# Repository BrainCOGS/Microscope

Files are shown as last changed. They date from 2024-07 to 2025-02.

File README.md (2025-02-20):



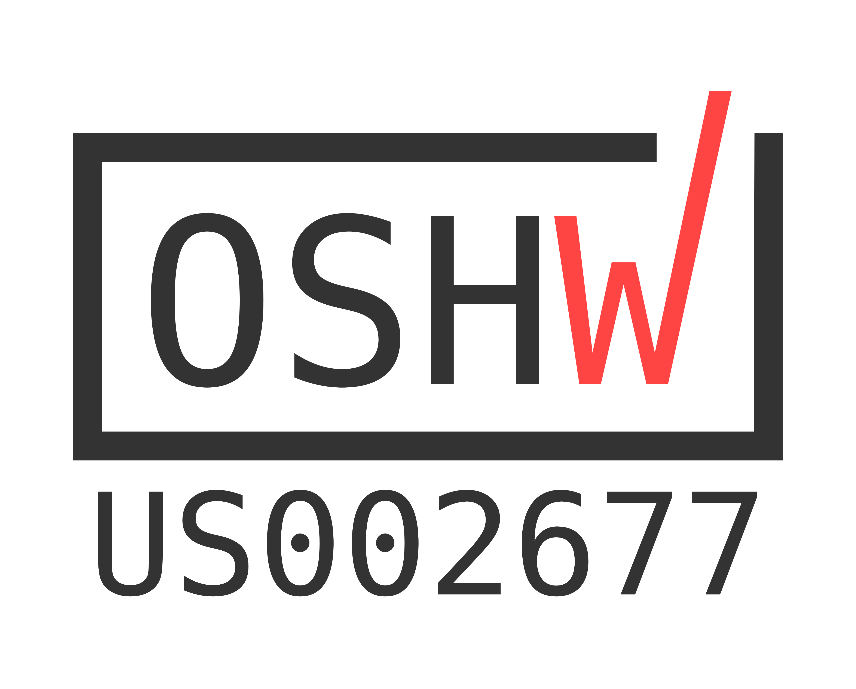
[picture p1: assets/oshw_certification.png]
# Twinkle 

This repository documents a microscope for Two-photon Imaging in Neuroscience, and Kit for Learning and Education — "Twinkle". <br/> It offers an affordable solution for a fully open, high-performance and cost-effective research and teaching microscope. Here, you can find the complete design and documentation. 

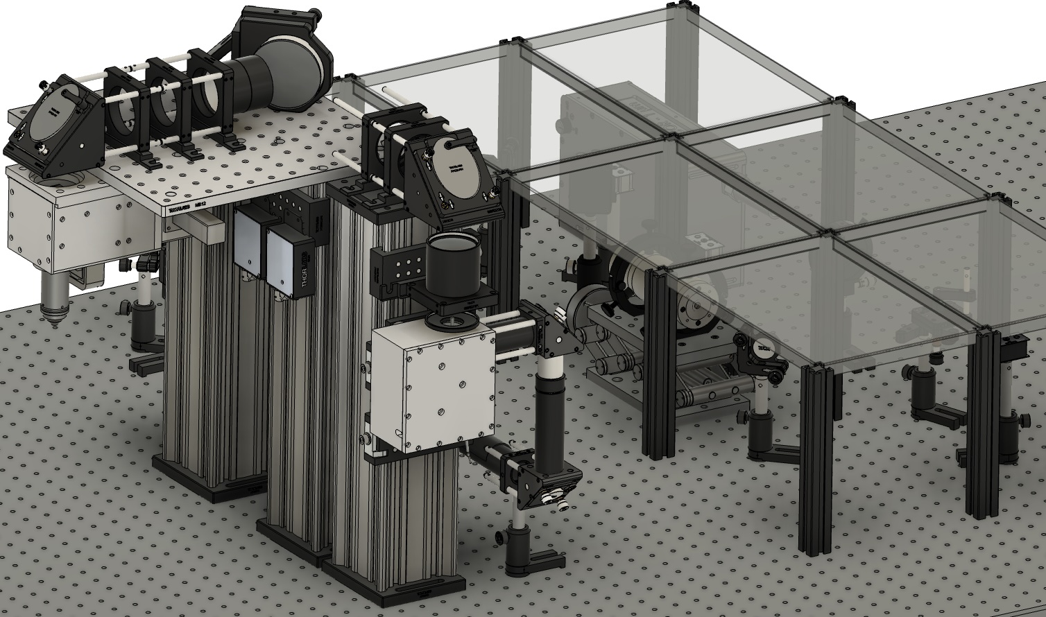
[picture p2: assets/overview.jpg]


### Repository Content
    .
    ├── article                 # Latex code and figures for the main manuscript.
    ├── assets                  # Supporting files, OSHW certification.
    ├── cad                     # Computer-aided design (CAD) files of the entire instrument in various file formats.
    ├── documentation           # Build instructions and supplemental material.
    ├── parts                   # Detailed bill of materials (BoM), important quotes, and drawings for machining.
        ├── Drawings            # Drawings for machining.
        ├── various files       # BoM and important quotes.
    ├── zemax                   # Optics simulations.
        ├── Collection          # Zemax files, drawings, and simulated performance of the collection optics.
        ├── Excitation          # Zemax files, drawings, and simulated performance of the excitation optics.
        ├── matlab              # Matlab scripts, using the Zemax API, measuring the performance of the excitation system.
    ├── LICENSE                 # Text file: This work is licensed under a CC Attribution 4.0 International License.
    ├── README.md               # Text file: This info file.
    └── okh-manifest.yml        # Text file: Open Know-How manifest files.   

### Computer assisted design (CAD) files
The CAD files are provided in two formats:
- In the Fusion 360 native format as `FullAssembly.f3d`; md5 hash `2b449ca0403f2ce7f2882990966d1d5e`.
- For Autodesk Inventor:
    1. When using the Inventor folder, open the master assembly `FullAssembly.iam`.
    2. A zip file of the same data is split into three files. Assemble the data with `cat x?? > FullAssembly.zip`. The file `FullAssembly.zip` is 165 MB with md5 hash `33ba62a7fb04bc53d11bb660787301d2`.

### Issue
Issues are tracked through this repository. For minor updates, just push. For major ones, use a PR. 

### License
This work is free: you can redistribute it and/or modify it under the terms of the Creative Commons Attribution 4.0 International license, version 4 of the License, or (at your option) any later version (CC-BY-4.0). This program is distributed in the hope that it will be useful, but WITHOUT ANY WARRANTY, to the extent permitted by law; without even the implied warranty of MERCHANTABILITY or FITNESS FOR A PARTICULAR PURPOSE. A copy of the License is provided in this repository.  For more details, see <http://www.gnu.org/licenses/>.

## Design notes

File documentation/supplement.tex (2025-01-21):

% Template for PLoS
% Version 3.5 March 2018

\documentclass[10pt,letterpaper]{article}
\usepackage[top=0.85in,left=2.75in,footskip=0.75in]{geometry}

% amsmath and amssymb packages, useful for mathematical formulas and symbols
\usepackage{amsmath,amssymb}
\usepackage{changepage}
\usepackage[utf8x]{inputenc}
\usepackage{textcomp,marvosym}
\usepackage{cite}
\usepackage[usenames,svgnames,table]{xcolor}
\usepackage[colorlinks = true,
            urlcolor = RoyalBlue,
            citecolor = Crimson,
            backref= page]{hyperref}
\usepackage[right]{lineno}
\usepackage{microtype}
\DisableLigatures[f]{encoding = *, family = * }
\usepackage[table]{xcolor}
\usepackage{array}
\newcolumntype{+}{!{\vrule width 2pt}}

\usepackage{figchild}
\usepackage{enumerate}
\usepackage{sidecap}
\usepackage{wasysym}
\usepackage{mathbbol}

% create \thickcline for thick horizontal lines of variable length
\newlength\savedwidth
\newcommand\thickcline[1]{
  \noalign{\global\savedwidth\arrayrulewidth\global\arrayrulewidth 2pt}%
  \cline{#1}%
  \noalign{\vskip\arrayrulewidth}%
  \noalign{\global\arrayrulewidth\savedwidth}%
}

% \thickhline command for thick horizontal lines that span the table
\newcommand\thickhline{\noalign{\global\savedwidth\arrayrulewidth\global\arrayrulewidth 2pt}%
\hline
\noalign{\global\arrayrulewidth\savedwidth}}

% Text layout
\raggedright
\setlength{\parindent}{0.5cm}
\textwidth 5.25in 
\textheight 8.75in

\usepackage[aboveskip=1pt,labelfont=bf,labelsep=period,justification=raggedright,singlelinecheck=off]{caption}

\bibliographystyle{plos2015}
\makeatletter
\renewcommand{\@biblabel}[1]{\quad#1.}
\makeatother

\usepackage{lastpage,fancyhdr,graphicx}
\usepackage{epstopdf}
\pagestyle{fancy}

\fancyhf{}
\rfoot{\thepage/\pageref{LastPage}}
\renewcommand{\headrulewidth}{0pt}
\renewcommand{\footrule}{\hrule height 2pt \vspace{2mm}}
\fancyheadoffset[L]{2.25in}
\fancyfootoffset[L]{2.25in}
\lfoot{\today}

%% Include all macros below
\newcommand{\microns}{~\textmu m~} % ALL UNITS UPRIGHT WITH SPACE
\newcommand{\invivo}{\textit{in vivo}~}
\newcommand{\complexi}{i}
%% END MACROS SECTION

\begin{document}
\vspace*{0.2in}

{
\centering\Large\textbf{Supplemental Online Material} 
}
\newline\newline
This supplemental material to the article ``TWINKLE: An open-source two-photon microscope for teaching and research'' describes the assembly, function and alignment of all parts of the microscope. Technical specifications are provided through the CAD files and the Zemax simulations in the online repository at \url{https://github.com/BrainCOGS/Microscope}.

\tableofcontents
\newpage

\linenumbers

\section{Preface}

\subsection{Safety}
Class 4 lasers are extremely dangerous. A reflection on a surface can be enough to inflict permanent eye damage. Safety protocols must be observed. Consult with your institution's environmental health and safety officer and take proper training before performing any work with a laser system. Learn from people experienced with these devices and work carefully.\newline
During alignment, always wear goggles (ours were ML1 by NoIR LaserShields with an optical density $>7$ in the relevant range around $920\text{ nm}$), remove jewelry and watches, only use non-reflective tools, do not store unnecessary items on the optical table, and use the low laser power (“alignment mode”) whenever possible. Once the assembly progresses further, full power mode is necessary. Extra care must be taken then. Always use Laser Viewing Cards to track the laser. We use Thorlabs VRC4. Always be conscious where the beam is, and where the beam goes. The beam must be terminated in beam blockers and should be shielded whenever possible with opaque plastic or anodized aluminium tubes to increase safety.

\subsection{Miscellaneous tools and tips}
The following tools are used throughout the build process:
\begin{itemize}
    \item A high quality duster to remove any residue from optical surfaces. We use a Miller-Stephenson Aero-Duster Ultra MS-222L, in addition to lens tissues (MC-5, Thorlabs) and Methanol (Sigma-Aldrich).
    \item To glue optical filters we used an extra fast setting epoxy (Hardman Double/Bubble Epoxy). To seal small gaps, we use black silicone putty (V-tie self-setting silicone rubber).
    \item We used either McMaster or Thorlabs screwdrivers and hex keys.
    \item For alignment, we used laser viewing cards (VRC4, Thorlabs), cage system alignment plates (VRC4CPT, Thorlabs), and irises (SM1 Graduated Ring-Actuated Iris Diaphragm, SM1D12C, Thorlabs).
\end{itemize}
%
The following general tips might be of help as well:
\begin{itemize}
    \item Shield the beam as soon as alignment of a particular section is done. This increases safety, and avoids accidentally bumping into aligned components.
    \item \textit{Walking the beam}: Any beam can be aligned through two irises using two mirrors. The first mirror the beam meets is sometimes called the ``position'' mirror as it affects primarily the position of the beam. The second ``angle'' mirror instead primarily affects the angle. Assigning each mirror a separate function (position versus angle) and by adjusting them iteratively, is a good rule of thumb for driving the beam through the 2 irises and eventually hitting a specific point at the desired angle \cite{Thorlabs}. 
    \item Be mindful of reflections from all surfaces. Put back-reflecting component at a slight angle to the beam (e.g. the half wave plate) to avoid back-reflections directly into the laser. The back-reflection can then be caught with an iris placed in front of the laser.
    \item Make sure the beam is at the same height across the table. This can be done with an iris and an IR card. 
    \item Take extra care for directing the beam through the center of all lenses and active optical components.
\end{itemize}

\subsection{Parts and bill of materials}
All custom metal pieces are parts of the CAD assembly of the microscope. Ours were manufactured from aluminium stock in the university machine shop. Aluminium has the added benefit of anodization, which can help control scattered light. An overview of the microscope's cost is shown in Tab.~\ref{tab_costs}. Keep in mind that these prices can significantly change over time, while some products can become unobtainable and need to be replaced with a different or newer model.
%
\begin{table}
\begin{center}
  \begin{tabular}{ l c r } \hline
   \textbf{Item} & \textbf{Info} & \textbf{Cost} \\ \hline
\rowcolor{gray!20} 920 nm fs-pulsed Laser  & Spark Alcor 920 + Warranty & 90 k \\
                   ScanImage DAQ-System \& optimized PC & MBF Bioscience& 20 k \\
\rowcolor{gray!20} Piezo collar & Physik Instrumente & 16 k	\\
            $2\times$ PMTs + preamplifiers  & Hamamatsu \& Thorlabs & 12 k \\
\rowcolor{gray!20} Pockels cell             & Conoptics &	11 k \\
                   Objective                & Nikon &  8 k \\
\rowcolor{gray!20} Machining custom parts   & Machine Shop; as per CAD files &  7 k \\
                   Optical filters          & AVR optics \& Semrock &  7 k \\
\rowcolor{gray!20} Lenses + optomechanics   & Thorlabs \& Newport &  7 k \\
                   Galvo-Resonant Scanner set & Novanta &  6 k \\
\rowcolor{gray!20} Electronics/cables/tools & Newark \& McMaster &  5 k \\
                   Mounting rack            & Emcor Enclosures &  3 k \\
\rowcolor{gray!20} Laser shutter            & Uniblitz/Vincent &  2 k \\
                   Laser safety goggles     & Edmund Optics &  1 k \\
\rowcolor{gray!20} Laser power meter        & Coherent &  1 k \\
                   Agarose \& fluorescent beads     & Thermofisher &  1 k \\
  \hline
 \textbf{Total}                    & & \textbf{197 k} \\
  \hline
  \end{tabular}
\end{center}
\caption{\textbf{Overview of the approximate cost in US-\$ (2024).} Note that this list excludes the optical table, and any other infrastructure costs such as compressors for air, and associated power supplies. This is just a summary. The detailed bill of materials is provided in the git repository.}\label{tab_costs}
\end{table}

\subsection{Structure and use of this document}
In the following sections, we will cover the setup and alignment of the microscope. This is split into three parts. The first part covers all components on the optical table that serve to condition the beam. The second part focuses on the  95 mm vertical post that holds the scanning mirror and scan lens assemblies. The third part is the microscope head with the attached collection optics. We will begin with the assembly on the optical table. All along, we assume the reader will have downloaded and opened the CAD model as we will rely heavily on it. Further, check carefully the instruction manuals of the scanning mirrors, photomultiplier tubes (PMTs), power supplies, Pockels cell, ScanImage, the Piezoelectric objective collar, and the filter mounting instructions.\newline
Before building your own microscope, read these instructions fully. Check the CAD files, and make sure that the instructions make sense. This document follows closely our own alignment procedure, and we have done our best to be accurate. However, use common sense. Do not follow these instructions blindly (or you might follow these instructions blindly in the future). Like all open instrumentation (under CC-BY-4.0), this work is distributed in the hope that it will be useful, but WITHOUT ANY WARRANTY, to the extent permitted by law; without even the implied warranty of MERCHANTABILITY or FITNESS FOR A PARTICULAR PURPOSE. 

\section{Assembly on the optical table}
%
\subsection{Beam conditioning}
An overview of the system for beam conditioning is shown in Fig.~\ref{sfig1} with key items labeled by capital letters. The following lines will cover the items, and their alignment.
%
\begin{figure}[!t]
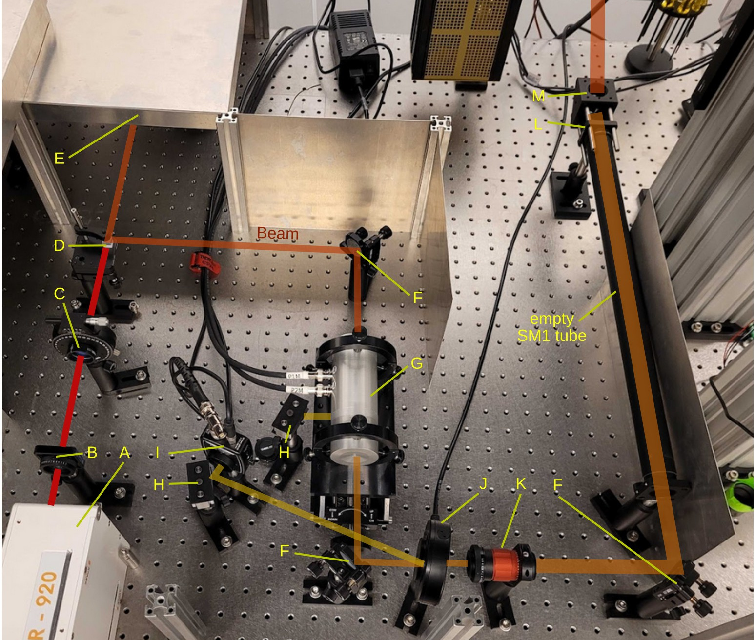
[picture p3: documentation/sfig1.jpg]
    
    \caption{{\bf Overall view of the beam conditioning path on the optical table.} Shown is a photograph of the components used to condition the beam for our microscope. Key components of the system are labeled with capital letters. The laser is shown as a red transparent line with intensity color coded. The beamsplitter cube (component D) splits the beam into two, halving its power. The Pockels cell (component G) reduces the power further. The reflections out of the Pockels cell and from the shutter (item J) are shown in yellow. The telescope (item K) magnifies the beam $\times 2$. The empty SM1 tube is an anodized aluminum SM1 lens tube cover (SC600, Thorlabs). All parts are explained in the text together with a note on their alignment.}
    \label{sfig1}
\end{figure}
%
\begin{enumerate}[]
    \item \textbf{A)} Laser head emitting the laser beam (red).
    
    \item \textbf{B)} Iris (SM1 Graduated Ring-Actuated Iris Diaphragm, SM1D12C, Thorlabs) inside a SM1-Threaded 30 mm cage plate (CP33, Thorlabs).
    
    \item \textbf{C)} $\diameter1\text{ inch}$ mounted achromatic half-wave plate with SM1-threaded mount (AHWP10M-980, Thorlabs) inside a high-precision rotation mount (PRM1, Thorlabs). First, use an iris to check that the beam travels centrally through the half-wave plate. Then place the half-wave plate at a slight angle to make sure that the beam reflected of the surface of the half-wave plate does not travel back into the laser. Confirm by using a detector card to find the (weak) back reflection. While doing this, terminate the beam traveling through the half-wave plate with a beam block.
    
    \item \textbf{D)} 10 mm polarizing beamsplitter cube (PBS103, Thorlabs) on a kinematic platform mount (KM100B, Thorlabs) held in place with a large adjustable clamping arm (PM4, Thorlabs). Arrows on the cube indicate which way the beam should go in and where the split beams travel. Similar to the half-wave plate, confirm that the reflection does not travel back to the laser using a detector card. Then adjust the kinematic mount to make sure that the transmitted and split beams travel parallel to the optical table. This is best checked with an iris far after the cube, and a detector card. Finally, adjust the angle on the half-wave plate such that transmitted and split beams have equal power. This has to be done at full-power mode of the laser. We used a Coherent FieldMaxII with a PM10 Thermopile power sensor.
    
    \item \textbf{E)} Beam block (hidden under the aluminium shield). This blocks the second beam which is not in use in our system (LB1, Thorlabs).
    
    \item \textbf{F)} $\diameter1\text{ inch}$ protected silver mirror (PF10-03-P01, Thorlabs) inside a kinematic mirror mount (KM100, Thorlabs): Reflects the beam.
    
    \item \textbf{G)} Pockels cell (350-80-LA-02 with 302RM driver, Conoptics) sitting on a holder (M102A, Conoptics). Properties of light travelling through this device are controlled electrically through the two connected wires. The alignment of the Pockels cell requires two steps: The Pockels cell has to be aligned with the optical axis of the laser, and be rotated relative to the laser's polarization such that the dynamic range is maximized \cite{Conoptics2018, Scientifica2024}. The first step can be done with an alignment tool of identical geometry to the Pockels cell (Conoptics modulator alignment tool 103). The second step requires the Pockels cell to be connected, and a power measurement performed. Importantly, these steps have to be done under full power because the beam profile in alignment mode might be slightly different from the full beam.
    \begin{itemize}
        \item First, install the holder on the table, and position on it the Conoptics Pockels cell alignment tool (Conoptics modulator alignment tool 103).
        \item Use a power meter on the output side, maximize power going through the central bore by manipulating the 4 bottom screws on the holder.
        \item Then switch the laser to full power and optimize the position of the screws for maximum transmission.
        \item Tighten the screws around the alignment tool, and mark on the screws the optical position. This will be important later to reproduce the exact same position of the alignment tool with the Pockels cell.
        \item Connect the Pockels cell (M350-80-LA, Conoptics) to the driver as per the Conoptics instructions (\texttt{p1m} and \texttt{p2m} go to \texttt{J1m} and \texttt{J2m}, \texttt{p1} and \texttt{p2} go to the controller). The controller settings are shown in Fig.~\ref{sfig2}.
        %
        \begin{SCfigure}
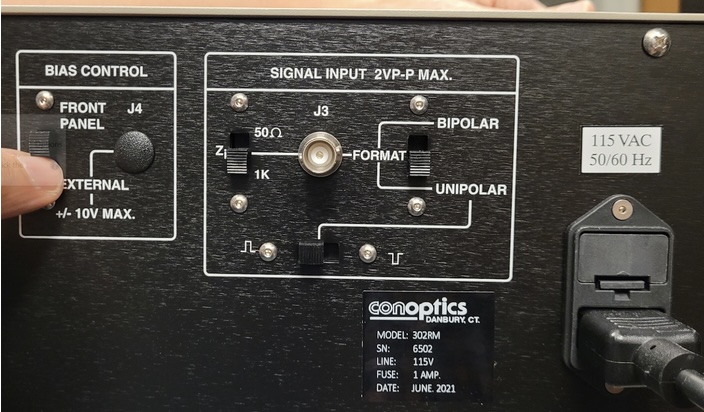
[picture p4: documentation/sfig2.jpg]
            
          \caption{{\bf Settings on the Pockels Cell controller.} Shown are the controls of the Pockels Cell driver as set in our system. For reference, see \cite{Conoptics2018}. We recommend for people building a microscope to take many such pictures of all settings and elements.}
          \label{sfig2}
        \end{SCfigure}
        %
        \item Next, determine the best orientation of the Pockels cell: For several rotations of the Pockels cell, measure its transmission while turning the dial on the Conoptics controller from one end to the other. Iterate this for different orientations of the Pockels cell until an optimum is found at which the dynamic range is greatest. This optimal orientation allows to adjust the laser power in the widest range. An example of different transmission curves is shown in the main manuscript, Fig. 9A. 
        \item The Pockels Cell splits the input beam into a transmitted and a rejected beam. The transmitted beam is used, while the energy of the rejected beam is dissipated in a beam block. By changing the control voltage of the Pockels Cell, the power ratio between the transmitted and rejected beam can be adjusted. The rejected beam leaves the Pockels cell through a bore at its side. During alignment, make sure that the rejected beam is properly terminated with a beam block.
        \item To validate the alignment, compute the extinction ratio of the Pockels cell, i.e. the ratio of maximal and minimal light transmission, and compare that number with the data sheet provided by Conoptics. Ours operate in a regime of $\approx 450$.
        \item Next, set the Pockels cell controller to the control voltage corresponding to minimum light transmission.
        \item Tighten the holder, and confirm that the Pockels cell is still well-aligned.
    \end{itemize}
    
    \item \textbf{H)} Two beam blocks (LB1, Thorlabs). Confirm that the right beam block terminates the rejected beam leaving the Pockels cell. The left beam block is used for calibrating the Pockels cell in ScanImage (the control software used by our microscope \cite{Vidrio2022, Pologruto2003}), together with a light sensor (I).

    \item \textbf{I)} Si Switchable Gain Detector, 350 - 1100 nm (PDA36A2, Thorlabs). This is used for the laser power calibration  of the light transmitted through the Pockels cell.  The detector is facing the beam block (H) and monitors the light that comes from the shutter back reflection when closed. Make sure that the gain on the detector is chosen reasonably for laser power and ambient light level. In our system, a gain of 50 dB works well. If the ambient room light is too bright, a SM1-mounted infrared long-pass filter in front of the photodiode can help (e.g. FELH0850, Thorlabs). The goal of setting the gain is well-defined sigmoidal control curve in ScanImage: Light transmission through the Pockels cell starts at a minimum, and increases as the Pockels control voltage increases.
        
    \item \textbf{J)} 6 mm Shutter (LS6S2ZM1, Vincent Associates) connected to driver (VCM-D1, Vincent Associates) for control of the shutter during imaging. To check that the shutter is properly aligned leave it open and make sure that the beam is not clipped. When closed, the back-reflection is sent to a beam block. For this reason the shutter is not mounted exactly perpendicular to the incident beam but at a slight angle. 

    \item \textbf{K)} $2\times$ Beam expander ($2\times$ Achromatic Galilean Beam Expander, GBE02-B, Thorlabs, inside SM1RC, Thorlabs). Aligning the beam expander requires two steps. First, it has to be aligned on the beam axis. Second, the beam needs to remain collimated after the beam expander, which is achieved by tuning the expander collar. For the first alignment, we use two irises, one screwed in the front, and one (on a reasonably long SM1 extension tube) behind the expander. The beam expander has to be positioned such that the beam travels through both iris, and such that the irises cut into the beam symmetrically. Next, we need to adjust the collimation of the beam using the expander collimation collar. It needs to be tuned so that the beam is the same size at the exit and after a long distance using several mirrors, see Fig.~\ref{sfig3}. 
    %
    \begin{SCfigure}
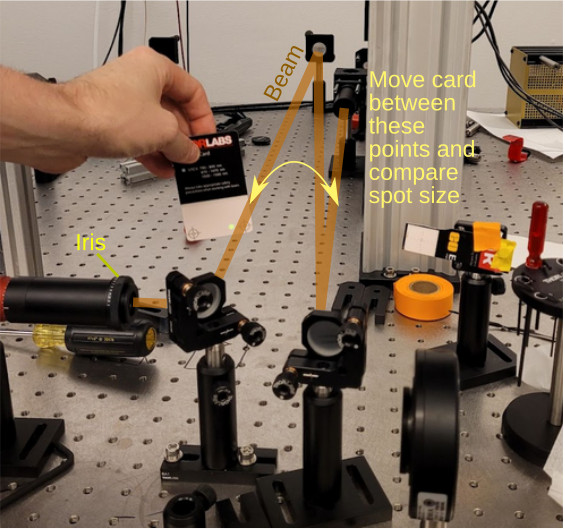
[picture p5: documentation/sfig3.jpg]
        
      \caption{{\bf Method for making sure the beam is collimated.} Using a set of mirrors, the beam (yellow line) can be reflected back and fourth to increase the distance travelled. Along this path (in this example of $\approx 2.5\text{ m}$), the beam must not change size ($<1\text{ mm}$). This is validated with an IR detection card and switching between the forward and return path of the beam. This method allows to control beam divergence after the $2\times$ telescope to below 1 mrad.}
      \label{sfig3}
    \end{SCfigure}
    %
\item \textbf{L)} Iris (SM1D12C mounted on a CP08 plate, both Thorlabs) used to check alignment.

\item \textbf{M)} Mirror (PF10-03-P01, Thorlabs, inside KCB1) to reflect the beam up at a right angle. For the next steps (in particular finding the optimal scanning mirror position), it is important that the beam travels up perpendicularly to the optical table, and parallel to the 95 mm optical rail column that holds the scanning mirrors (next section).

\end{enumerate} 
%
When finished aligning the beam through all the optical components listed above, clamp them down on the table securely. Then shield the beam path with additional SM1 and SM2 tubing, and tubing cover (e.g. Thorlabs SC600, SM1 Anodized Aluminum Lens Tube Cover) to increase safety and to protect the aligned optical components.
%
\subsection{Assembly of the scanning post}

\subsubsection{Components}

Following beam conditioning on the optical table, the beam is reflected up from the optical table towards the ceiling into a box housing the scanning mirrors. This is shown in Fig.~\ref{sfig4}A,B. Following the scanning mirrors, the beam travels up through the scan lens, and directed to the microscope head with another mirror.
%
\begin{figure}[h]
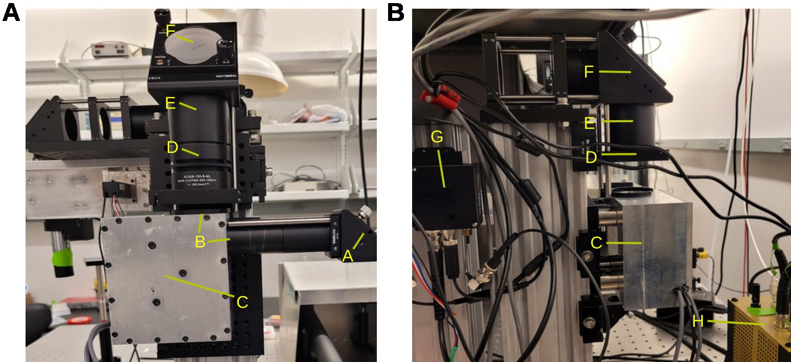
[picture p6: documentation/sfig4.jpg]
    
    \caption{{\bf Overall view of the scanning post.} \textbf{A)} Side few. Key components of the system are labeled with capital letters. These are explained in the text together with a note on how to align these components. Importantly, the machined block (C) houses the scanning mirrors, and the scan lens assembly is placed in the SM2 house labeled (E). \textbf{B)} Frontal view. The PMT preamplifiers (component G) and the scanning mirror power supply (component H) are visible.}
    \label{sfig4}
\end{figure}
%
%
\begin{enumerate}[]
    \item \textbf{A)} Mirror (PF10-03-P01, inside KCB1, with CP12 attached) - turn the beam at a right angle.
    \item \textbf{B)} Broadband filter (WG11010-B, Thorlabs, inside SM1L20 and SM1S20) - filter to keep dust out of the box housing the scanning mirrors.
    \item \textbf{C)} An aluminium box containing the resonant and slow galvanometer set (CRS8K/6215H Resonant-Galvo Set, Novanta), mounted to 95 mm rail (XT95RC4, Thorlabs). A detailed description is provided below.
    \item \textbf{D)} Empty tubing (SM2V05, adjustable SM2 Lens Tube, Thorlabs).
    \item \textbf{E)} Scan lens - See detailed description below.
    \item \textbf{F)} Mirror in its housing (PF20-03-P01 and KCB2, both Thorlabs). While we used a round $\diameter2\text{ inch}$ mirror, this should be replaced with an elliptical mirror and housing (PFE20-P01 and KCB2EC, both Thorlabs). This would increase the field-of-view because the cross-section of an ellipse at 45 degrees is a circle. At low magnification, a round mirror will lead to vignetting.
    \item \textbf{G)} PMT preamplifier (TIA60, Thorlabs) attached to a 95 mm rail.
    \item \textbf{H)} Power supply for the scanning mirrors (part of the Novanta scanning mirror set) housed in an electronics prototype box.
\end{enumerate}

\subsubsection{Alignment}

\begin{itemize}
    \item First, mount the 95 mm rail to the table. Then attach a bracket (all from the XT95 series, Thorlabs) to the side to hold the scan lens (component D in Fig.~\ref{sfig3}), and one on top with a cage system to hold a mirror (component F in Fig.~\ref{sfig3}). For alignment with cage systems, we use a cage system alignment plate (VRC4CPT, Thorlabs). The rest of the assembly here will be done without any lenses. The goal is a well-aligned beam that travels through the center of all parts, and parallel to the optomechanical surfaces.
    \item The box housing the scanning mirrors is connected, trough SM1 tubing, to a mirror (component A in Fig.~\ref{sfig3}). To align this upper periscope mirror with the lower periscope mirror, mounted on the table, connect a piece of SM1 tubing to the upper mirror facing down, and  a second piece of SM1 tubing to the table mirror facing up (component M in Fig.~\ref{sfig1}). These two pieces meet in mid-air. The gap in between can be reduced to zero using adjustable length SM1 lens tube (e.g. SM1V10, Thorlabs, not shown in CAD) and can be further closed by a small piece of  lens tube cover (SC600, Thorlabs). 
    \item Next, we adjust the mirror (component A in Fig.~\ref{sfig4}A) so that light travels through the center of the scanning mirrors and up the 95 mm rail. This is done with irises. One is attached at the entry port of the scanning mirror box, e.g. in the SM1 tube (component B in Fig.~\ref{sfig4}A). Another two irises are attached, as far away as possible, to a 95 mm rail bracket. It is convenient to use the future holder of the scan lens (component D/E in Fig.~\ref{sfig4}). This ensures that the beam will pass through the center of the scan lens. As the mirror (component F in Fig.~\ref{sfig4}) is not installed yet, an IR detection card can conveniently be taped to the ceiling to make sure that the beam is on-axis. Of note, the resonant scanner is at its origin point when no power is being provided, but the slow galvanometer needs to be provided 0 V to position the mirror at its origin point. This can be done through the voltage supply, or to a good approximation through ScanImage by setting the scan mode to the highest possible zoom level. In our microscope design, it can be helpful to wiggle the lid to which the scanning mirrors are mounted (item C in Fig.~\ref{sfig4}). This step is tricky and can require some patience. 
    \item When confirmed that the light travels parallel to the 95 mm rail, we attach the mirror (component F in Fig.~\ref{sfig4}), and slide it along the cage rods to a position where the beam is reflected centrally through the caging system and the mount positioned on top of the 95 mm rail. This is done using the same set of two SM2-mounted irises that we used to make sure that light leaves the scanning mirror box without x or y displacement. The beam is now ready to travel through the microscope head.
\end{itemize}

\subsection{Assembly of the microscope head}
%
A picture is shown in Fig.~\ref{sfig5}.
\subsubsection{Components}
%
\begin{figure}[t!]
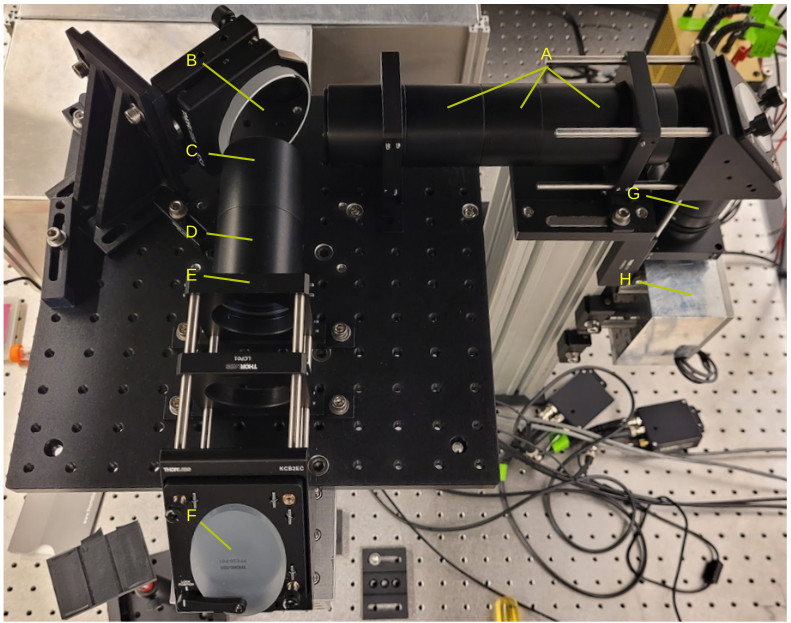
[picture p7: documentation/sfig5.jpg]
    
    \caption{{\bf Overall view of the microscope head.} Key components of the system are labeled with capital letters. These are explained in the text together with a note on how to align these components.}
    \label{sfig5}
\end{figure}
%
\begin{enumerate}[]
    \item \textbf{A)} Empty tube, shielding the beam aligned in the previous section.
    \item \textbf{B)} Protected silver Mirror (PF30-03-P01, Thorlabs) inside KS3 and clamped down with XE25CL2 and another clamp. This mirror directs the beam through the tube lens. We will refer to this part as ``big mirror''. This is the first mirror that we will have to align.
    \item \textbf{C)} Tube lens - See detailed description below.
    \item \textbf{D)} Empty, just a tube used for spacing because the distance between the scan lens, tube lens, and objective is important.
    \item \textbf{E)} Tube holder (LCP01, Thorlabs) - just there to hold the lens straight, use with ER series 6 mm rods (ER6-P4, Thorlabs).
    \item \textbf{F)} Elliptical mirror (PFE20-P01 inside KCB2EC, both Thorlabs). We will refer to this part as ``collection mirror''. This is the second mirror that we will align.
\end{enumerate}
%
%
\subsubsection{Setup and alignment}

\begin{itemize}
    \item Mount the two 95 mm posts to the table.
    \item Mount the collection optics box to the aluminium stage, and then mount the stage to the 95 mm rail. Do not install the photomultiplier tubes yet. These devices are light sensitive, and more alignment needs to be done before we are ready to install them.
    \item Equip the aluminium stage with brackets and cage mounts to hold SM2 tubing (A, D and E in Fig.~\ref{sfig5}).
    \item First, we position the big mirror at a $45^\circ$ angle (component B in Fig.~\ref{sfig5}). Place two irises after the big mirror, one at the future position of the tube lens (component C in Fig.~\ref{sfig5}) and one far away beyond the future position of the collection mirror (component F in Fig.~\ref{sfig5}). Aligning the big mirror is fiddly, but can be achieved with small adjustments of its position in x and y, and the tilt of its housing. We found it helpful to use a 45 degree angled rod to guide the mirror in the direction parallel to its surface. Whichever method is used, this step can take some time. Importantly, do not adjust the set screws of the mirror on the scanning post (component F in Fig.~\ref{sfig4}) because that is already aligned.
    \item Install the collection mirror (component F in Fig.~\ref{sfig5}). Then position an iris in place of the future objective, and a second iris as far away as possible just above the optical table. Use an adapter with external $\text{M}32\times0.75$ threads and internal SM1 threads (SM1A33, Thorlabs) to attach the irises to the objective collar. Then shift the collection mirror along the rail and adjust its tilt via the set screws so that the beam is aligned with the two irises.
\end{itemize}

\subsubsection{Scan and tube lens alignment}

After the beam's alignment is confirmed by traveling through the two irises, it is time to install, and align scan and tube lens. Remember that (1) the distance between the tube lens (component C in Fig.~\ref{sfig5}) and scan lens (component G in Fig.~\ref{sfig5}) has to be 100 mm + 375 mm = 475 mm while (2) the scanning mirror set (component H in Fig.~\ref{sfig5}) has to be positioned in the focal plane of the scan lens (see Fig. 1 in the main manuscript). In our design, the objective is fixed. Therefore we have to perform the lens alignment in several steps, conceptually beginning at the back-aperture of the objective. 

\begin{itemize}
    \item Before starting, make sure the lens groups in the tube and scan lens assembly are mounted correctly. Specifically, when inserted into one of our previously aligned SM2 mounting rings, they should focus the beam, but must not incur a lateral or angular displacement. To test this, one can screw them into component E in Fig.~\ref{sfig5}, and observe the beam far away on a wall. The lens groups must not change the position of this spot, only its size. Only proceed if the lens groups were assembled and mounted correctly.
    \item The first lens group to be installed is the tube lens assembly. Position the tube lens such that the beam, at maximum zoom level, is focused at the back-aperture plane of the objective. As the objective is not installed yet, an IR detection card can be placed at its future location. We designed the microscope such that the tube lens assembly is to be mounted on a 1 inch long SM2 extension to the cage plates (Component D in Fig.~\ref{sfig5}. See also the diagram in the section on ``Tube lens Assembly'' below). Observe how the focal plane changes when moving the tube lens along the optical rails (Component E in Fig.~\ref{sfig5}). When its correct position is confirmed, tighten the set screws on the optical cage.
    \item Next, install the scan lens above the scanning mirror box. The spacing between tube lens and scan lens is critical because the beam leaving the tube lens has to be collimated. To test this, remove the elliptical mirror (component F in Fig.~\ref{sfig5}) from its housing, and observe the spot on a wall far away, while moving the scan lens up and down on the 95 mm optical rail. Find a position at which the beam neither converges, nor diverges after the tube lens, and the spot on the wall has the same size as the beam right after the tube lens. Only then is the beam well collimated. Clamp down the scan lens on its rail.
    \item Next, reinstall the elliptical mirror (component F in Fig.~\ref{sfig5}), and observe the back-aperture of the objective, while moving the scanning mirror box up and down. The scan mirrors have to be positioned in so that they are conjugated to the back aperture of the objective. It is positioned correctly when the well-collimated light converges on the back aperture of the objective across scan angles. Make sure that (1) no beam clipping is visible on high zoom along the optical path. (2) In the conjugated plane of the scan lens, a nice and crisp plane should be visible on an IR card, produced by the scanning beams focused down to a point. (3) The fast resonant scan combined with the slow scan gives the beam a visible dynamic, a ``wobble''. If the scanning mirror box is positioned correctly, then, the beam at the objective back aperture will not translate while scanning because all deflection angles converge on the back aperture (cf. Fig. 1 in the main manuscript). In other words, the ``wobble'' becomes minimal at the plane conjugated to the scan mirrors. Notice how adjustment of the scan mirrors relative to the scan lens can bring this conjugate plane to any point below the collection optics. Now, adjust the height of the scanning mirror box to a point so that the minimal-wobble plane is located at the back aperture of the objective and clamp down the scanning mirror box. For a useful illustration of this method, see also \cite{Yao2023}. Of note, this step of fine-tuning the position of the scan box up and down along the 95 mm optical rail is the reason why we stressed the importance of the alignment of the scanning post, the components A in Fig.~\ref{sfig4} and M in Fig.~\ref{sfig1} earlier. It was critical that across the various heights used here, the scanning mirror box was precisely aligned with the beam.
    \item Shield the beam with more SM1 and SM2 tubing to protect the beam from misalignment, the optics from dust, and the user from accidentally exposing themselves to the beam.
\end{itemize}
%
\subsection{Installing objective and photomultiplier tubes}
%
\subsubsection{Components}
%
\begin{SCfigure}
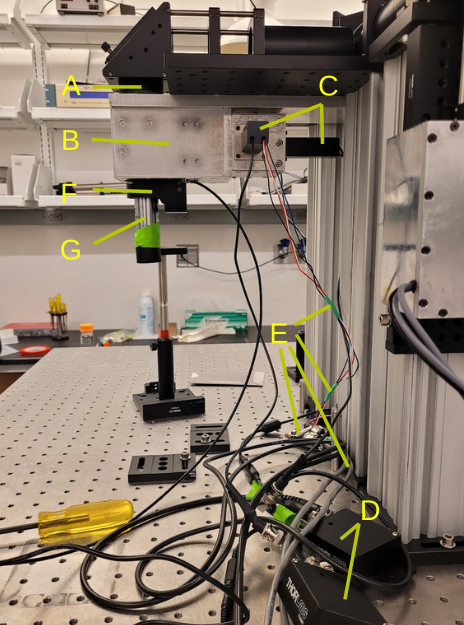
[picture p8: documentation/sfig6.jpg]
    
  \caption{{\bf Side view of the microscope head.} Key components of the system are labeled with capital letters. These are explained in the text together with a note on how to align these components.\newline
  Set up like this, we were measuring the amount of light traveling through the system. Note the detector taped to the objective with green tape.\newline
  Also note that the photomultiplier tubes (component C) are light sensitive and need to be installed in the dark. We recommend to switch off the room lights when handling them, and allowing your eyes to adapt to the dark over several minutes. After installation into the collection optics, the lights can safely be used. The objective is easy to install, and just screwed into the piezoelectric collar, component F.}
  \label{sfig6}
\end{SCfigure}
%
The optics and optomechanics are now essentially in working order. The last missing steps towards a working microscope are the installation of the objective, and the photomultiplier tubes. These elements are visible in a side view of the microscope head, see Fig.~\ref{sfig6}.
%
\begin{enumerate}[]
    \item \textbf{A)} Adjustable lens tube (SM2V05, Thorlabs), made flush with the collection box to stop room light entering the optics. Otherwise this will increase the background signal during use of the microscope. 
    \item \textbf{B)} Aluminium box housing the collection optics - See detailed description below.
    \item \textbf{C)} Two photomultiplier tubes (``PMTs'', Hamamatsu H16201-40). Their shielded output cable (black) and the control and power supply cables (color-coded wire) are also visible.
    \item \textbf{D)} PMT Transimpedance Amplifier (Thorlabs TIA60) - amplifier for the PMTs. Set the output offset on the PMT amplifier such that no signal equals 0 V. The amplifiers are directly connected to the PMT output on the input and ScanImage on the output.
    \item \textbf{E)} Control signals and power supply for the PMTs going to the custom PMT control box.
    \item \textbf{F)} Piezoelectric objective collar (P-725K085: PIFOC(R) 400 \textmu m travel, Physik Instrumente).
    \item \textbf{G)} The microscope's objective (Nikon N16XLWD-PF, Thorlabs).
\end{enumerate}
%
\subsubsection{Objective installation}
Before installing the objective, double check that the beam is collimated below the piezoelectric collar, and on-axis. To do so set the ScanImage zoom level to high and with the use of two irises confirm that the beam is not clipped. Then screw the objective into the collar.
 
\subsubsection{PMT installation}
PMTs are light sensitive. Always store them with their aperture covered with blackout tape when not in use (AT205-1.0 black aluminium foil tape, Thorlabs). When removing the tape for installation, this installation into the collection box must be done in darkness and as quickly as possible. We recommend to use black silicone putty (V-tie self setting silicone rubber), and have it ready for use to seal the gap between the PMTs and the aluminium box. Switch the room lights off, wait a few minutes to adapt to the darkness then mount the PMTs on their respective ports. Of note, when ordering the PMTs from Hamamatsu, one can request PMTs with particularly low dark count and high quantum efficiency to reduce noise. We typically request a quantum efficiency of at least 45\% at 520 nm, and a dark count of 4000 cps or below at 25 degree Celcius.

\subsection{Shield the light path}
Now that your microscope is ready, finish shielding the light path with SM1 and SM2 tubing, lens tube cover (SC600, Thorlabs), and cover the optical table with sheet metal. We use bent 1 mm aluminium sheet, placed on small columns made from T-slotted rail.

\section{Last steps}
%
\subsection{No signal?}
If no picture is visible, check:
\begin{itemize}
    \item Is a fluorescent sample under the objective? A bright simple will be useful, such as a fluorescent plastic slide (FSK5, Thorlabs). Is the sample positioned in a suitable distance from the objective? Note that the focal plane is only a few \textmu m wide. If no fluorescence is produced in this optical slice, no signal will be visible in ScanImage.
    \item If the objective requires water immersion, has a drop of water been placed between the sample and the objective?
    \item Are all beam blocks removed from the path? Check with IR cards along the way. Below the objective, the IR light should be focused to a tight spot.
    \item Are the PMTs operating as intended? This can be checked with a light-source like a flashlight close to the objective. This should noticeably increase the noise in the picture.
\end{itemize}
%
\subsection{Validation and tuning}
%
Validation and tuning is done in several steps.
\begin{itemize}
    \item The first sample to image should be a fluorescent plastic slide (FSK5, Thorlabs). These are bright and uniform. It can be helpful to scratch the surface of the slide to find a feature to focus on. With this sample, the group delay dispersion can be adjusted for maximum signal. It should also validate that the field-of-view is as intended, and no obstructions exist in the beam path.
    \item Next, image a calibrated scale to validate the microscope's magnification. We used a reference slide featuring a 100 \textmu m grid (Thorlabs R1L3S3). This slide was covered with a drop of Fluorescein solution in water and a standard coverslip. Find the calibration grid, and compute the magnification in \textmu m/pixel. It should be approximately equal in x and y direction. Our microscope has sufficiently small field curvature that despite the thin film of dye, the entire grid should be visible. An example is shown in Fig.~\ref{sfig7}A.
    \item Next, measure (at very low laser power to not saturate the PMTs) the two photon intensity from a uniform bath of Fluorescein, see Fig.~\ref{sfig7}B. This measures field flatness. Alignment problems either in the excitation or collection path will make this image less uniform. Of note, small alignment errors in particular of the scan lens can have a major effect on field flatness. If your field is not as uniform as the example shown, we recommend to check the scan lens first.
    \item Finally, use a fluorescent bead sample to measure the microscope's point spread function (PSF), see Fig.~\ref{sfig7}C. This will reveal more subtle misalignment and aberration in the optics. We use a 5000:1 mix of 100 nm fluorescent beads (``Dragon Green'' 480/520 from Bangs Laboratories) in in 1\% Agarose. To prepare this sample, take the beads from the fridge, vortex the container, take the 10 \textmu l and 49.5 g of water. Then microwave the mix with 0.5 g of Agarose until the solution is clear. While warm, place a drop on a microscope slide, and cover with a coverslip. Bring your sample to the microscope, and record a z-stack. Use low laser power to not damage the beads, or saturate the PMTs. The example shown was recorded with 5\% laser power at 99.9 zoom for 40 z-slices with 0.5 \textmu m spacing. The PSF profile should be symmetric, and a faint, but also symmetric, Airy ring visible around the bead, around 5 \textmu m away from center of the bead (see Fig. 2D in the main manuscript).
\end{itemize}
%
\begin{figure}[!t]
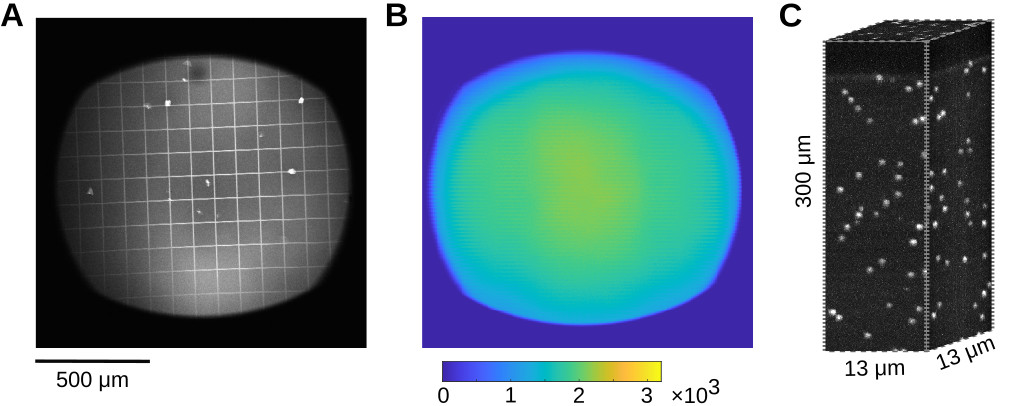
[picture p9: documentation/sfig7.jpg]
    
    \caption{{\bf Three key validation samples.} \textbf{A)} Image of a reference slide with a 100 \textmu m grid to measure the microscope's magnification. Note how the entire grid is in focus, suggesting small field curvature. \textbf{B)} Two photon intensity from a uniform bath of Fluorescein. This shows that the microscope can effectively elicit and collect fluorescence across the field of view. \textbf{C)} A volumetric image of fluorescent beads in Agarose. This is used to compute the axial and radial width of the microscope's point spread function. Use low laser powers for these measurements to not saturate the PMTs and to produce correct results.}
    \label{sfig7}
\end{figure}
%
%
\section{Assembly of subcomponents}
In the remaining sections, we will cover the microscope's sub-assemblies and their construction, beginning with the lens groups.
%
\subsection{Tube lens assembly}
The tube lens assembly is made of two cemented doublets $2\times$ ACT508-750-B (Thorlabs), see Fig.~\ref{sfig8}A. The letter ``B'' signifies that these lenses have an anti-reflective coating in the IR range. For assembly, the lenses are placed on a lens assembly tool, and a SM2 housing is lowered above them, for an example see Fig.~\ref{sfig8}B. This methods has to be used for the lenses to be seated correctly. The individual steps for the tube lens group are as follows:

\begin{itemize}
    \item Place the first element on top of the spanner wrench (Thorlabs SPW604) using lens paper. Check the lens thoroughly. Dust can be blown away with a duster, finger prints wiped off with Methanol and a lens cleaning tissue.
    \item Blow it with the air duster. 
    \item Slide the SM2L10 tube over the element until it sits in the end. Sometimes it needs to be wiggled, but do not force it.
    \item Flip the whole thing over.
    \item Now the element is in the tube. Tighten it with a SM2 retaining ring.
    \item Insert a second SM2 retaining ring for spacing. 
    \item Repeat the previous steps to install the second lens above the SM2 retaining ring
    \item Flip again, blow with air, and set the lens in place with a third SM2 retaining ring. This produces the configuration shown in Fig.~\ref{sfig8}A.
    \item Be careful with dust and fingerprints when putting elements into the tube. Confirm that there are no fingerprints, and no dust particles trapped on or between the lenses.
\end{itemize}
%
Our simulations indicate that the lens spacing between the two doublets is not critical, and the approximate clearance provided by two SM2 spacer rings is sufficient. This is shown in Fig.~\ref{sfig8}A. For more precise placement, a spacer ring like the one shown in Fig.~\ref{sfig8}B can be used. This will be important for the slightly more complex scan lens assembly described in the next section.
%
\begin{figure}[!t]
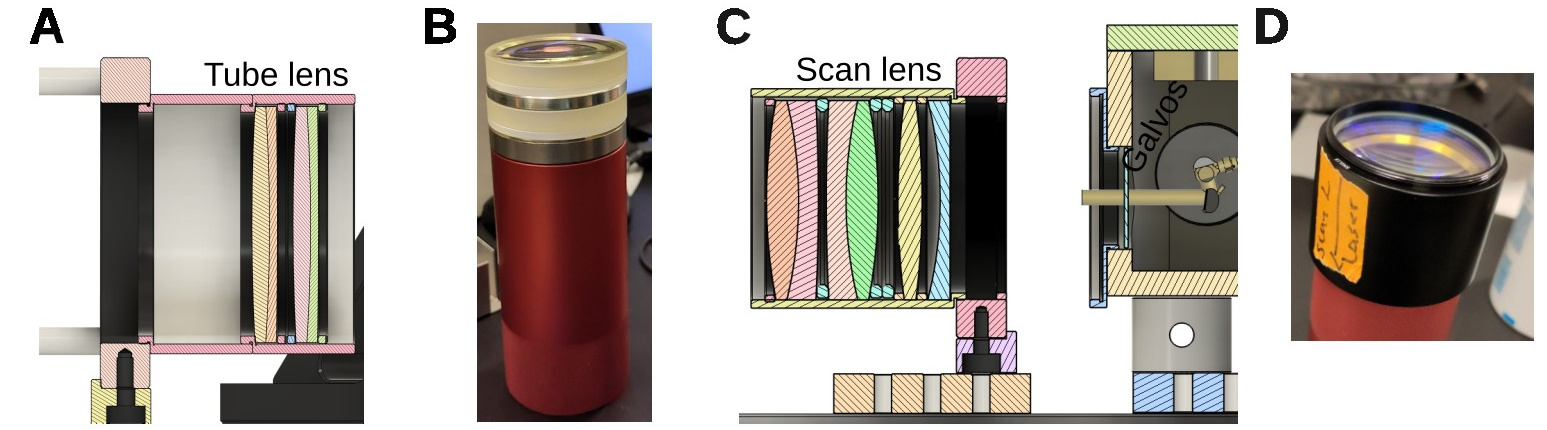
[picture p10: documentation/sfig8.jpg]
    
    \caption{{\bf Assembly of lens groups.} \textbf{A)} Tube lens assembly with the two doublets held in place with spacer rings. \textbf{B)} Assembly method of lenses: Lenses and spacer rings are stacked on a SM2 spanner, ready for the SM2 tubing to be lowered around them. \textbf{C)} Design of the scan lens assembly. Notice the custom spacer rings in blue. The distance between the last element of the scan lens assembly and the scanning mirror box is $\approx 1.35 \text{ inch}$. \textbf{D)} The assembled scan lens group in its SM2 housing.}
    \label{sfig8}
\end{figure}
%
\subsection{Scan lens assembly}
The scan lens assembly is shown in Fig.~\ref{sfig8}C. The individual steps for the scan lens group are as follows:
\begin{itemize}
    \item Place the KPC070AR, a plano-concave lens, on the spanner wrench with the plane side facing out. Check the lens thoroughly for dust and finger prints.
    \item Slide the SM2 tube over the elements until they sit at the end of the tube. Sometimes it needs to be wiggled, to make sure the lenses are seated properly.
    \item Flip the whole thing over.
    \item Tighten it with a SM2 retaining ring.
    \item Next, place the LB1199-B lens on the wrench. This is a bi-convex lens for which the orientation is irrelevant. Flip over the assembly, and tighten the lens with a second SM2 retaining ring. 
    \item For the third and fourth lens, place an ACT508-200-B lens, a spacer ring, the second ACT508-200-B lens, and two spacer rings on the wrench. Make sure you remove all dust from the various surfaces. Flip over the assembly, and tighten the lens with a third SM2 retaining ring. 
    \item Check the assembly for trapped dust or fingerprints. This will produce a lens group like the one shown in Fig.~\ref{sfig8}D.
\end{itemize}

\subsection{Assembly of the collection optics}
%
The collection optics are made from several components, including optical filters, lenses, and custom metal pieces. Fig.~\ref{sfig9}A shows a cut through the CAD drawing. The function is described in the main manuscript. A pictures of the collection optics box is shown in Fig.~\ref{sfig9}B with key components labeled. Here, we will focus on the assembly and their alignment.
%
\begin{figure}[h]
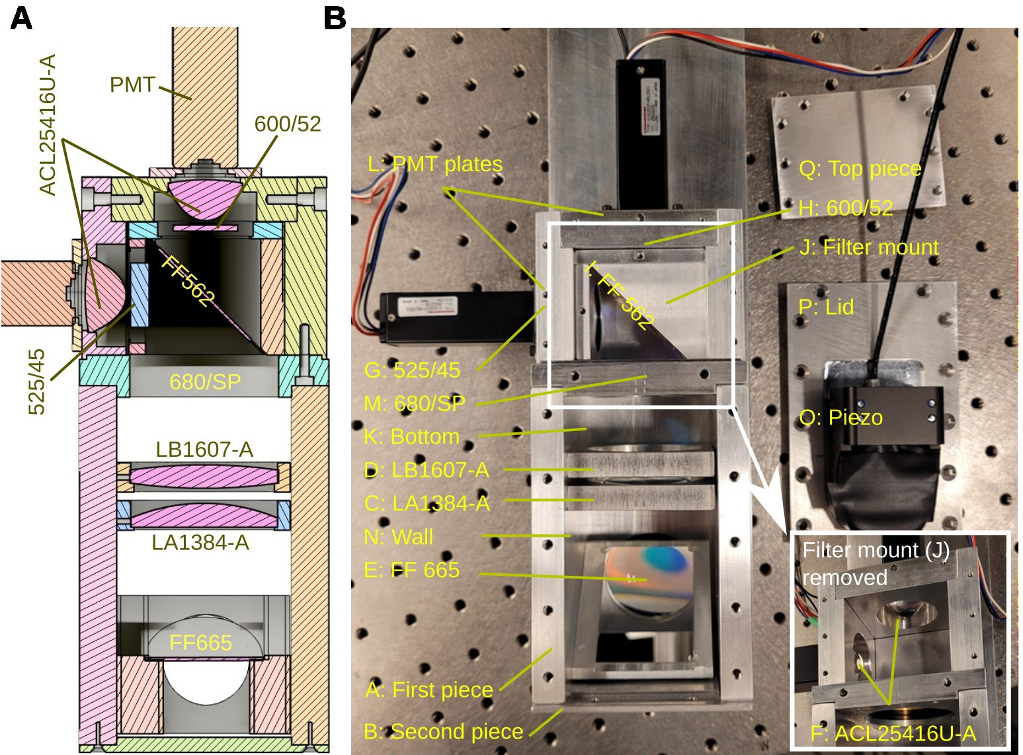
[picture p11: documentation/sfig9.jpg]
    
    \caption{{\bf Assembly of the collection optics.} \textbf{A)} The assembled collection optics with bottom cover removed, perspective from below. \textbf{B)} The collection optics during the assembly process, similar to panel A. Key components are labeled (see text). EDITS TO MAKE IN THE ARROWS}
    \label{sfig9}
\end{figure}
%
\begin{enumerate}[]
    \item \textbf{A)} The construction of the collection optics box starts with a side panel attached to the base with stainless steel button head hex screws, 8-32 thread size, 1/2 inch long.
    \item \textbf{B)} Next, we attach the front panel. This is connected  with stainless steel Phillips flat head screws, 82 degree countersink angle, 4-40 thread size, 1/8 inch long and undercut.
    \item \textbf{C)} Then we install the first lens, a LA1384-A plano-convex lens (Thorlabs), see Fig.~\ref{sfig9}. The flat side of the lens sits against the lip inside of its aluminium holder. The convex side points towards the PMTs. The lens is glued in place with three dots of Epoxy (because 3 points make a plane, and 4 can bend the lens). When gluing, make sure to dab the glue on and pull AWAY from the center of the mirror. That way any glue strands do not fall onto the mirror. When the glue has set, the holder is screwed into the wall. 
    \item \textbf{D)} The next lens to be installed is a biconvex lens (LB1607-A, Thorlabs). This lens is symmetric, so can be oriented in any way. It is also epoxied on three spots and the holder screwed into the wall, see Fig.~\ref{sfig9}A.
    \item \textbf{E)} Next, we glue the first dichroic mirror to its holder. This dichroic mirror separates IR light from fluorescence (FF665-Di02-40X55, AVR Optics). Its orientation is important. The caret points TOWARDS the metal piece. The filter is then glued in place with three dots of Epoxy, and the triangular holder screwed into the wall.
    \item \textbf{F)} Next, we fix the condenser lenses (ACL25416U-A, Thorlabs) in their housing plates. The convex part is facing towards the inside of the box, and set with nylon set screws (Stainless Steel Nylon-Tip Set Screw, 4-40 thread size, 1/8 inch long). The holders are then fixed together with stainless steel socket head screw, 8-32 thread size, 3/8 inch long.
    \item \textbf{G)} With the condensers in place, we can install the optical band-pass filters in front of them. First the 525 nm band-pass filter (Semrock Brightline FF01-525/45-32, AVR Optics) for the green channel, which is secured with a nylon set screw (stainless steel nylon-tip set screw, 4-40 thread size, 1/8 inch long). Orientation is important: For this brand of filters, the arrow is following the light path, i.e. away from the inside of the box and towards the PMT.
    \item \textbf{H)} Next we install the 600 nm band-pass filter for the red channel (Semrock Brightline FF01-600/52-32, AVR Optics). Like the 525 nm filter, it is secured with nylon set screws and the arrow points away from the inside of the box and towards the PMT.
    \item \textbf{I)} Next, we attach the dichroic mirror that splits red and green light (Semrock Brightline FF562-Di03-40X52, AVR Optics) to its metal holder. The caret points towards the metal holder, such that the side the caret is pointing to contacts the metal when it is glued in place. When the glue has set, the mirror casing is screwed in place using stainless steel socket head screw, 4-40 thread size, 5/16 inch long. The glue used is a 5 min non-sagging Epoxy. Three dichroic was attached with 3 points of glue of minimal volume.
    \item \textbf{J)} The piece containing the 525 nm and 600 nm band-pass filters and the dichroic mirror is connected to the larger metal box with stainless steel socket head screw, 4-40 thread size, 3/4 inch long.
    \item \textbf{K)} The bottom piece (bottom per the view of the picture in Fig.~\ref{sfig9}B) of the PMT box is attached using 4-40 thread size, undercut, 3/16 inch long screws.
    \item \textbf{L)} PMT plate. The PMT attaches to the flat side of the PMT plates with 4 specialized low profile screws (CBSTSR2-6, Misumi). The other side has a shallow cut out for the screw head to sit. The plate with the PMT attached screws into the rest of the assembly using 4-40 thread size, 5/16 inch long socket cap screws.
    \item \textbf{M)} Next, we install an IR block filter (Semrock BrightLine Multiphoton Filter FF01-680/SP-50, AVR Optics). This filter is sandwiched between two rings (SM2RR).
    \item \textbf{N)} Then we close the second panel with 8-32 thread size, 1/2 inch long socket cap screws.
    \item \textbf{O)} The piezoelectric holder is attached to the aluminium part using the adapter that comes with it. Be careful to not damage the Serial Cable connected to the holder.
    \item \textbf{P)} The lid is attached using 8-32 thread size, 3/8 inch long, undercut screws. Finish off by securing the rest of the front plate screws (component B) using 4-40 thread size, 1/8 inch long screws. Screw in the piece holding M to the lid using 4-40 thread size, 1/2 inch long socket cap screws.
    \item \textbf{Q)} Attach the top cover using 4-40 thread size, undercut, 3/16 inch long screws.
\end{enumerate}
%
\subsection{Assembly of the scanning mirror housing}
%
\begin{figure}[!t]
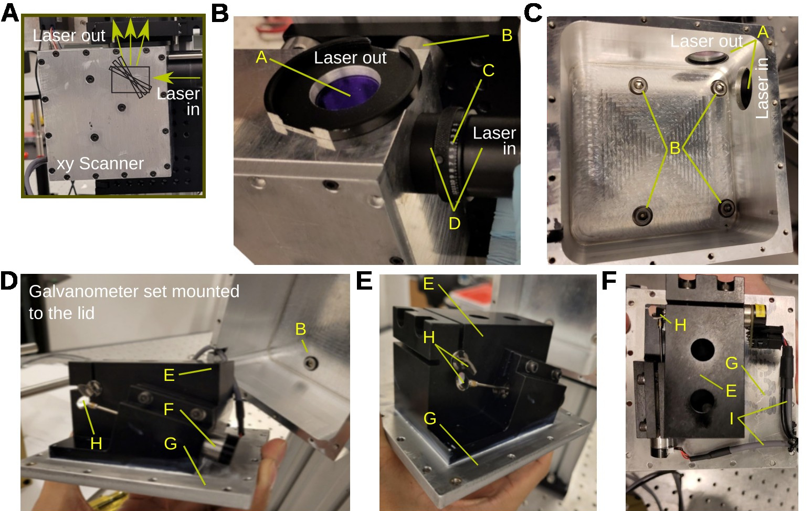
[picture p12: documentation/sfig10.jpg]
    
    \caption{{\bf The scanning mirror box.} \textbf{A)} The custom aluminium box housing the pair of scanning mirrors. \textbf{B)} Close-up of the same box with key parts labeled: A: Two windows (WG11010-B, Thorlabs) to keep dust out. B: Attachment of the box to the 95 mm optical rail. C: An Iris used for alignment, and D: SM1 tubing. \textbf{C)} Bottom part of the aluminium box. A: the windows, and B: screws to attach the box to the drop-on rail carriage via four 3/4 inch tall $\diameter1\text{ inch}$ diameter posts. \textbf{D)} The scanning mirrors are mounted to the lid using heat transfer compound. E: Anodized aluminium block holding the scanning mirrors. F: One of the scanning mirror assemblies, G: The aluminium lid and H: The scanning mirrors. \textbf{E)} Same as \textbf{D} but different angle. \textbf{F)} Same as \textbf{E} but different angle. I: Cables controlling the scanning mirrors.}
    \label{sfig10}
\end{figure}
%
The scanning mirror housing is a machined piece of aluminium holding the Novanta scanning mirror set against the 95 mm optical rail (XT95, Thorlabs), see Fig.~\ref{sfig10}. It also shields the scanning mirrors from dust in the environment, and protects the environment from audible noise produced by the resonant scanning mirror. The housing is composed of a box, mounted to the 95 mm rail (Fig.~\ref{sfig10}A,B,C), and a lid to which the Novanta scanners are mounted (Fig.~\ref{sfig10}D,E,F). When mounting the black anodized holder, make sure to apply heat transfer compound between the holder and the lid (we use Wakefield Thermal Joint Compound Type 120-5 Silicone, cf. Fig.~\ref{sfig10}D,E). While the resonant scanner does not dissipate much heat, the slow galvanometer becomes warm in normal operation, and this heat needs to be dissipated. This is particularly important when pushing to fast responses, and driving the slow galvanometer with larger currents.\newline

The two box apertures (beam input and output) have near-infrared antireflection-coated flat BK7 windows (WG11010-B, Thorlabs) secured with SM1 tubes and retaining rings (SM1RR, Thorlabs). We used a SM1 to SM2 converter ring at the exit, Fig.~\ref{sfig10}B, to ease checking alignment with downstream mounts and optics.

\subsection{Scanning mirror power supply}
%
The scanning mirrors come with driver circuit boards. We place them in a prototype box (EG6, Gold Box, Acopian), and connect the driver board's power supply and signal lines to connectors for easier access, see Fig.~\ref{sfig11}A. The driver boards are mounted to the aluminium walls of the prototype box with heat transfer compound (Wakefield Thermal Joint Compound Type 120-5 Silicone). The power connectors accept banana plugs. The signals are connected to BNC connectors. 
%
\begin{figure}[t]
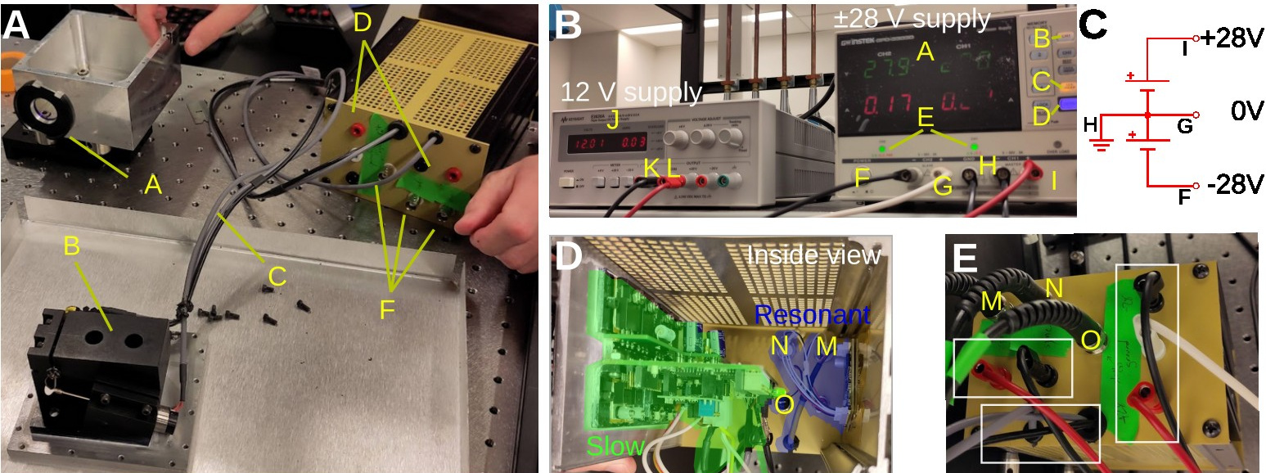
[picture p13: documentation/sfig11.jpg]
    
  \caption{{\bf Scanner electronics.} \textbf{A)} Overview of all scanning mirror parts. Key parts are labeled with capital letters. Optomechanics were covered in Fig.~\ref{sfig10}. All electrical drivers were placed in the yellow circuit box. \textbf{B)} Power supply and connection of the scanning mirrors with key parts labeled by capital letters. \textcolor{black}{\textbf{C)} Wiring diagram for the $\pm 28\text{ V}$ power supply, using two galvanically isolated supplies. \textbf{D)} The scanning mirror driver boards, provided by Novanta, and mounted in the yellow circuit box. The smaller driver circuit (blue) powers the resonant scanner. The larger circuit board (green) drives the slow galvanometer. The circuit boards are mounted to the aluminium walls with screws and heat transfer compound. \textbf{E)} Same box as in D, but from the outside and key parts labeled by capital letters.}}
  \label{sfig11}
\end{figure}
%
Fig.~\ref{sfig11}A shows as the housing box (component A) and xy scanning mirror set (component B) that we discussed above. Components C are the cables connecting the scanning mirrors to their driver boards. These driver boards are housed in a yellow prototype box, and connected to accept power (component D), and signals (component F). Fig.~\ref{sfig11}B shows the power supply of the scanning mirrors. At time of purchase, we requested the controller of the slow galvanometer mirror to be configured for usage at $\pm 28\text{ V}$ (manufacturer default is $\pm 24\text{ V}$). This overall improves dynamical properties. The controller for the slow scanner requires three supplies respectively: -28 V, 0 V, and +28 V. \\
\textcolor{black}{To provide these three signals, we used a power supply with two galvanically isolated and adjustable output channels, that can be connected in series (Note: not every power supply supports this function. We used a GPD-3303D from Gw Instek that allows this function with the SER/INDEP key). The voltage of each of the two unconnected channels was set to +28 V. To produce the three supply signals, we used these two channels in series. In other words, we connect the positive terminal of the first channel to the negative terminal of the second channel. As the channels are otherwise not connected to a common ground (this is meant with the words ``galvanically isolated''), this does not produce a short circuit. Instead, this link effectively provides a new reference point, relative to which the first supply produces a negative -28 V supply, and the second supply produces the +28 V supply. This is illustrated in Fig.~\ref{sfig11}C. In this arrangement, a multimeter would read between points G and I +28 V, between G and F -28 V, and between F and I +56 V. The supply of the resonant scanners is simpler, as it only requires a single +12 V line. The supplies are connected to the power supply ports on the prototype box, in which the two driver boards reside, see Fig.~\ref{sfig11}D. Signal lines are connected on the outside with coaxial cables to the MBF Bioscience DAQ system, see Fig.~\ref{sfig11}E.} Key components in the panels are labeled with capital letters. These are as follows:
\begin{itemize}
    \item \textbf{A)} Power supply (GPD-3303D, Gw Instek) with two channels configured in series, both set to 28 V.
    \item \textbf{B)} Have CH 1 turned on.
    \item \textbf{C)} Press the ``Ser/Indep'' button. This wires the two channels together to a shared references to provide the $\pm 28\text{ V}$ and the 0 V reference line, see Fig.~\ref{sfig11}C.
    \item \textbf{D)} This button enables our power supply unit. Only when pressed, power is sourced to the galvanometer driver board.
    \item \textbf{E)} CC/CV indicator light. Make sure that the device is set to CV (constant voltage).
    \item \textbf{F)} The -28 V output line (black). This is connected to the -28 V line on the electronics box (shown below in Fig.~\ref{sfig11}E).
    \item \textbf{G)} The reference lines, 0 V (white) connected to the 0 V line on the electronics box, see Fig.~\ref{sfig11}E.
    \item \textbf{H)} Connects the reference line to ground.
    \item \textbf{I)} The +28 V output line (red) connected to the +28 V line on the electronics box. Conform the correct voltage with a reliable multimeter BEFORE powering up the galvanometer controller, e.g. with a Fluke 117.
    \item \textbf{J)} Power supply (E3630A, Keysight) set to 12 V to power the resonant scanners.
    \item \textbf{K)} Black cable is the reference, and connected to black port on the controller box. Just below the connectors M/N/O.
    \item \textbf{L)} Red channel, set to +12 V, is connected to the red port on the controller box. Just below the connectors M/N/O.
    \item \textbf{M)} Coaxial connector controlling ``Zoom'' (the resonant scanners's amplitude).
    \item \textbf{N)} Coaxial connector for ``Sync'' (the resonant galvanometer's digital synchronization signal)
    \item \textbf{O)} Coaxial connector for controlling the slow galvanometer.
\end{itemize}
Make sure the power supply settings are correct before plugging in the scanning mirrors. Confirm this independently with a reliable multimeter (e.g. Fluke 117) and do not just trust the display. Of further note, the scanning mirror driver boards cannot be mixed and matched. Every board has a unique ID that is matched to the scanner. Double check that they are connected correctly before powering up.

\subsection{Assembly of PMT control circuits}
The last part to be assembled is the control circuitry for the photomultiplier tubes. This is shown in Fig.~\ref{sfig12}. The circuit is shown and explained in the main manuscript. Here, we will cover the assembly. In short, the circuit allows a user to set the gain of the H16201P-40 photomultiplier tube module with a potentiometer \cite{Hamamatsu2024}, while displaying the control voltage on a small digital panel meter (Murata DMS-20PC). The supply of this circuit is a well regulated +15 V supply that also powers the PMTs. The panel meter needs a +5 V supply that we obtain from the +15 V via a voltage divider. The PMT is supplied directly with the +15 V. It also sources a signal through the blue cable that is connected to ground via a voltage divider, using a potentiometer. This voltage divider produces the control voltage that is fed back to the module via the white input line, and used for display on the panel meter. Due to the simplicity of this circuit, we do not solder this on a circuit board, but rather in a prototype development box directly, see Fig.~\ref{sfig12}A,B, which is attached to the rig.
%
\begin{figure}[t]
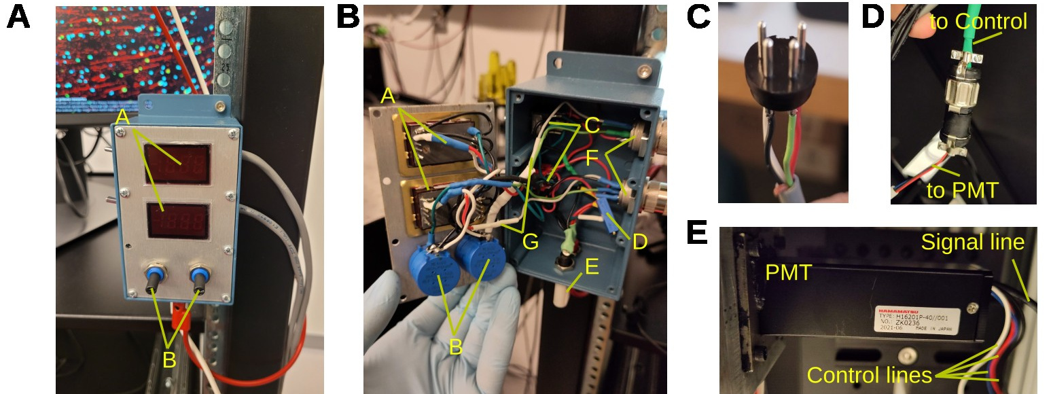
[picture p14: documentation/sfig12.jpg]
    
  \caption{{\bf Custom electronics.} \textbf{A)} Picture of the control box. Component A are the displays for the control voltage for red and green channels. Component B are the two potentiometers to set the two channel gains. \textbf{B)} Inside view of the potentiometer box with key components labeled (see text). \textbf{C)} Connector attached to the controller box before plugging into the PMTs. \textbf{D)} Connector from the Control box to the PMT cables. \textbf{E)} Outputs of the PMTs. Note the four color-coded American wire gauge \#28 cables, and the coaxial signal line\cite{Hamamatsu2024}.}
  \label{sfig12}
\end{figure}
%
The first components to be wired up are the Murata DMS-20PC displays. The circuit diagram is shown in the main manuscript Fig. 4.
\begin{itemize}
    \item Solder pins 7 and 8 together on each of the two displays. The displays are component \textbf{A} in Fig.~\ref{sfig12}A,B.
    \item Solder 2.5 inch long and 5 inch long pieces of wires to pin 12 on the top display.
    \item Solder the other end of the 2.5 inch long piece of wire and a new 1 inch long piece of wire to pin 3 (+5 V return).
    \item Solder the other end of the 1 inch long piece of wire, and add 1.5 inch and 3 inch long pieces to display pin 6 (DP1).
    \item Solder the other end of the 1.5 inch long piece and another 1 inch long piece to pin 3 (+5 V return) of the bottom display.
    \item Solder the other end of the 1 inch long piece and a new 2 inch long piece to pin 6 (DP1) of the bottom display.
    \item Solder the other end of the 2 inch long piece to pin 12 (input lo) of the bottom display.
    \item Solder the other end of the 3 inch long piece from pin 6 (DP1) of the top display and a new 12 inch long piece of wire to the middle pin of the left potentiometer.
    \item Solder a 12 inch long piece of wire to pin 3 (closest to the knob) on the left potentiometer (50 kOhm, 3590S-1-503L, Bourns). These are the two big blue parts, component \textbf{B}, in Fig.~\ref{sfig12}A,B.
    \item Solder a 12 inch long piece of wire and 5 inch long piece of wire to pin 11 (input hi) on the top display.
    \item Solder the other end of the 5 inch long piece of wire to pin 1 (furthest from the knob) on the left potentiometer.
    \item Solder a 5 inch long piece of wire to pin 1 and pin 2 (+5 V supply) of the top display.
    \item Solder the other end of the 5 inch long piece of wire to the middle pin on the side opposite to where it says ON/ON on the switch.
    \item Solder a 12 inch long piece of wire and a 5 inch long piece of wire to pin 11 (input hi) on the bottom display.
    \item Solder the other side of the 5 inch long piece of wire to pin 1 (further from the knob) on the right potentiometer.
    \item Solder a 12 inch long piece of wire to pin 3 (closest to the knob) on the right potentiometer.
    \item Solder a 12 inch long piece of wire and the other end of the wire connected to pin 12 of the top display to pin 2 (middle pin) on the right potentiometer.
    \item Solder a 6 inch long piece of wire to the middle pin on the side adjacent to where it says ON/ON on the switch (component \textbf{C}).
    \item Solder a 3 inch long piece of wire to the left pin (left with the words being oriented the correct direction) on the side adjacent to where it says ON/ON on the switch.
    \item Solder the other end of the 3 inch long piece of wire and a 12 inch long piece of wire to the left pin (left with words being oriented the correct direction) of the second switch on the side opposite to ON/ON words.
    \item Solder a 12 inch long piece of wire to middle pin on the second switch on the side opposite to the ON/ON words.
    \item Solder a 6 inch long piece of wire to left pin on the potentiometer used for the  +5 V supply of the display (component \textbf{D}).
    \item Solder a 6 inch long piece of wire to right pin on the same potentiometer.
    \item Solder a 4 inch long piece of wire to center pin on the same potentiometer. 
    \item Connect the left and right pins to the banana plugs and set the potentiometer to 5 V going across BEFORE connecting the middle wire to the rest of the controller circuit! 
    \item Solder the other end of the 4 inch long wire and another 4 inch long piece of wire to the middle pin on the second switch on the side adjacent to the ON/ON words.
    \item Solder the other end of the 4 inch long piece of wire to the right pin (right with words being oriented in the correct direction) on the side opposite to the ON/ON words on the first switch.
    \item Solder a 5 inch long piece of wire to the right pin (right with words being oriented the correct direction) on the side adjacent to where it says ON/ON on the second switch.
    \item Solder the other end of the wire to pin 1 and pin 2 (+5 V supply) on the bottom display.
    \item Trim the wires from the middle pin of the gain adjusters by around 5 inch, connect those two wires, the wire furthest from the dial on the potentiometer, and two 12 inch long wires by twisting together.
    \item Solder a 3 inch long wire to the white banana plug and screw it in the housing. This is component \textbf{E} in in Fig.~\ref{sfig12}B.
    \item Solder a 3 inch long wire to the red banana plug and screw it in the housing.
    \item Connect the twisted together wires to the white banana plug.
    \item Connect the wire closest to the dial on the potentiometer and the left pin (left with words being oriented in the correct direction) on the second switch on the side opposite to the ON/ON words to the red banana plug.
    \item Solder one of the wires from the white banana plug to pin 2 of the top 4-pin female connector. This connection is item \textbf{F} in Fig.~\ref{sfig12}B. The 4-pin connector that will plug into this port is shown in in Fig.~\ref{sfig12}C.
    \item Solder the wire from the pin closest to the knob on the left potentiometer to pin 3 of the top 4-pin female connector. Put a 12k Ohm resistor within the path of the wire (component \textbf{G} in white heat-shrink tubing). This limits the control voltage to approx. 0.8 V, which is safer for the PMT \cite{Hamamatsu2024}. We discuss this in the main manuscript.
    \item Solder the wire from pin 11 on the top display to pin 1 of the top 4-pin female connector (M16 4 Pin Connector).
    \item Solder the wire from the middle pin on side adjacent to ON/ON words on the top switch to pin 4 of the top 4-pin female connector.
    \item Do the previous 4 steps for the other 4-pin female connector.
\end{itemize}
%
This concludes the assembly of the control box. The connection of this box to the PMTs is made through a custom cable. A male connector, shown in in Fig.~\ref{sfig12}C, plugs into the control box on one end, and into a female plug soldered to the PMT module on the other. This is shown in in Fig.~\ref{sfig12}D. The PMT module has four colored control lines attached to, see in Fig.~\ref{sfig12}E, that are wired to this connector. The specific type, shown in Fig.~\ref{sfig12}D, is a Wire-Pro, Inc. (WPI) 126-195 connector.

\section{Software and control}
%
\subsection{Laser settings}
The laser control depends on the system used. The Alcor 920 laser is controlled through a USB interface, and software that runs on the same PC as ScanImage. The software is used to switch on the laser, switch between alignment and full-power mode, and to adjust the group delay dispersion. 

\subsection{Shutter settings}
The shutter controller has various settings that allow either manual control, or control via ScanImage. In our system, a ``Local/Remote'' toggle switch selects between those options. A second important toggle switch is ``N.O./N.C.''. In the ``N.C.'' position, the shutter will be activated open by an input pulse signal. In the ``N.O.'' position the shutter will be activated closed. If ScanImage's shutter control signal is not correctly actuating the shutter, very likely this toggle switch needs to be flipped.
%
\subsection{Setting up ScanImage}
%
\begin{figure}[t]
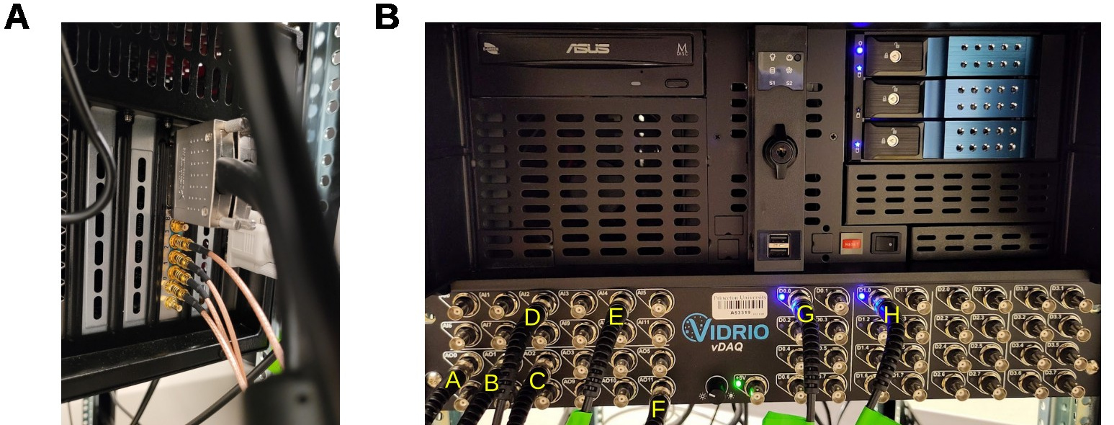
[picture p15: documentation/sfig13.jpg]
    
  \caption{{\bf Setup Vidrio DAQ system.} \textbf{A)} Wiring of the four input channels. These are connected to the PMT preamplifiers, and for our system digitized at 14 bit resolution. \textbf{B)} Data acquisition panel connected to the microscope's various control and signal lines. Capital letters are explained in the text.}
  \label{sfig13}
\end{figure}
%
At this point, all hardware is set up and aligned. The next step is configuring ScanImage, the software used to control the microscope \cite{Pologruto2003, Vidrio2022} to communicate with the various components. This is done through a number of coaxial lines that connect the Vidrio data acquisition system with the microscope hardware, see Fig.~\ref{sfig13}. Our system is connected, on the back, to the two PMT outputs, see Fig.~\ref{sfig13}A. The front panel links the system to eight signals, Fig.~\ref{sfig13}B. These are
\begin{itemize}
    \item \textbf{A)} \texttt{Analog-out}: X-resonant zoom control.
    \item \textbf{B)} \texttt{Analog-out}: Y-slow control.
    \item \textbf{C)} \texttt{Analog-out}: Piezo control for the objective collar.
    \item \textbf{D)} \texttt{Analog-in}: Piezo feedback from the objective collar.
    \item \textbf{E)} \texttt{Analog-in}: Pockels cell feedback.
    \item \textbf{F)} \texttt{Analog-out}: Pockels cell control.
    \item \textbf{G)} \texttt{Digital}: Resonant scanner sync.
    \item \textbf{H)} \texttt{Digital}: Shutter control.
\end{itemize} 
%
When connected, ScanImage needs to be configure to make use of these connections. The process is as follows.

\begin{itemize}
    \item Type \texttt{ScanImage} into Matlab and press Enter.
    \item Login using the correct credentials.
    \item Under \texttt{Machine Data File}, click \texttt{New}.
    \item Type in a filename and click \texttt{Save}.
    \item Select \texttt{Blank Configuration}.
    \item Next we need to add all the devices of the microscope. Start by clicking the \texttt{Devices} tab, and pressing \texttt{+} to add each new device.
    \item Shutter
    \begin{itemize}
        \item Select \texttt{Digital Shutter} and click \texttt{Add}.
        \item Type in a name like \texttt{Shutter1}.
        \item In the new window, select \texttt{/vDAQ0/D1.0} for \texttt{Control Channel}. This will depend on how you have wired up the control line to the front panel.
        \item \texttt{Open time (seconds)} remains at the default of 0.5 s.
        \item Check the \texttt{Invert Output} box.
        \item Click \texttt{Apply}.
        \item Make sure the shutter itself (on the driver box) is on \texttt{STD} for the key and the toggle switches (see above) are set to \texttt{N.C.} and \texttt{Remote}.
    \end{itemize}
    \item Pockels cell:
    \begin{itemize}
        \item Select \texttt{Pockels Cell} and click \texttt{Add}.
        \item Type in a name like \texttt{Pockels1}.
        \item In the new window, select \texttt{/vDAQ0/AO11} for \texttt{Control Channel}. Again, this will depend on the channel that the Pockels driver is connected to.
        \item For \texttt{Feedback Channel (optional)}, select \texttt{/vDAQ0/AI4}. This is connected to the photodiode directed at the beam block for the shutter. The gain should be chosen for a good signal. In our system, a gain of 50 dB works well. If the ambient room light is too bright, a SM1-mounted infrared long-pass filter in front of the photodiode can help (e.g. FELH0850, Thorlabs). The goal of setting the gain is sigmoidal control curve in ScanImage: Light transmission starts at a minimum, and increases as the control voltage increases.
        \item Under \texttt{Control output [Volt]}, change \texttt{Max} to \texttt{1.7}. This is the maximum control voltage applied to the Pockels cell driver.
        \item When calibrating, notice how it takes about 1.7 V to reach 100\% laser power.
        \item Leave the \texttt{Open shutters for calibration} field unchecked because our shutter is positioned after the Pockels cell and the reflection off the closed shutter used for calibration with a photodiode.
        \item Leave everything else in the \texttt{Basic} tab unchanged.
        \item Leave everything else in the \texttt{Calibration Settings} and \texttt{Advanced} tabs unchanged.
        \item Click \texttt{Apply}.
    \end{itemize}
    \item Slow galvanometer:
    \begin{itemize}
        \item Select \texttt{Analog Galvo} and click \texttt{Add}
        \item Type in a name like \texttt{Y-Galvo}
        \item In the new window, select \texttt{/vDAQ0/AO1} for \texttt{Control Channel}. This will depend on the port that the galvanometer is connected to.
        \item The rest of the defaults have to be adjusted as per the Galvanometer's specifications. For our slow galvanometer, these are as follows.
        \item Change \texttt{Volts per optical degree [V/deg]} to \texttt{0.7692}.
        \item Change \texttt{Angular range [optical degrees]} to \texttt{26}.
        \item Change \texttt{Park position [optical degrees} to \texttt{13}.
    \end{itemize}
    \item Resonant scanner:
    \begin{itemize}
        \item Select \texttt{Resonant Scanner} and click \texttt{Add}.
        \item Type in a name like \texttt{X-res}.
        \item In the new window select \texttt{/vDAQ0/D0.0} for \texttt{Sync Channel}. This will depend on your wiring.
        \item For \texttt{Zoom Control Channel}, select \texttt{/vDAQ0/AO0}.
        \item Leave everything else unchanged. We used a 8 kHz scanner.
        \item Click \texttt{Apply}.
    \end{itemize}
    \item Piezoelectric objective collar.
    \begin{itemize}
        \item Select \texttt{PI E709} and click \texttt{Add}.
        \item For \texttt{Serial port / USB}, select \texttt{COM1}.
        \item For \texttt{Control Channel}, select \texttt{/vDAQ0/AO2}. This will depend on your wiring.
        \item For \texttt{Feedback Channel}, select \texttt{/vDAQ0/AI2}. This will depend on your wiring.
        \item Click \texttt{Read From Device} and numbers should automatically update.
        \item Click \texttt{Apply}.
        \item Click \texttt{Calib} on the new Piezo widget.
        \item Should be able to feel piezoelectric mount vibrate with hand when it calibrates.
        \item Check \texttt{Enable Stack} on the main ScanImage window and the \texttt{STACK CONTROLS} windows should pop up.
        \item Better to do \texttt{step} instead of \texttt{sawtooth} for resonant scanner since we are averaging images; with \texttt{sawtooth}, we would be averaging difference Z depths together
        \item Select 10 \texttt{Frames per Slice}, 5 \texttt{Number of Slices}, 10 \texttt{Number of Volumes}, and 5 for \texttt{Step Size [um]}.
        \item Click \texttt{Test Waveform}.
        \item In new window, click \texttt{Optimize Waveform}.
        \item Ringing at the beginning and end of steps can be corrected with \texttt{Actuator lag}.
    \end{itemize}

    \item After adding the devices, we have to create an imaging system by clicking the \texttt{ScanImage} tab and click \texttt{+ Add Imaging System +}.
    \item In the new window, under \texttt{vDAQ Scan System}, click \texttt{Add} and type in a name like \texttt{My microscope}.
    \item In the new window, select \texttt{X-res} under \texttt{Resonant Scanner}.
    \item For \texttt{Y-Galvo}, select \texttt{Y-Galvo}.
    \item Check off \texttt{Use} for \texttt{Shutter1}.
    \item Check off \texttt{Use} for \texttt{Pockels1}.
    \item Check off \texttt{Use} for \texttt{Piezo1}.
    \item Under \texttt{Channel}, check off \texttt{Invert} for all 4 channels.
    \item Leave everything under the \texttt{Triggers}, \texttt{Advanced}, and \texttt{I2C} tabs unchanged. Of note: The setting \texttt{I2C} is used for syncing with behavior.
    \item Click \texttt{Apply}.
\end{itemize}
%

\section{Recommendations for use}
Make a point of regularly checking your microscope. Lenses can get dirty, the path misaligned, and components age.
%
\begin{itemize}
    \item Measure (1) the laser's power levels, (2) the Pockels cell calibration and (3) check exposed lenses and mirrors for dust and fingerprints with a flashlight. This is fast and should be done before every experiment.
    \item When the microscope is not in use, it is good practice to switch off all components, except the scanning mirror power supplies, the PMT preamplifiers, and the photodiode.
    \item Every once in a while, switch the red and green PMTs to check for signs of aging and validate their performance on a fluorescent slide or sample of known brightness. The PMTs can degrade and may need to be replaced, depending on use, after several years. They should be treated with care: power ramped up and down slowly, and saturation should be avoided. We use a rotation system in which new PMTs are typically used for the green channel. When their performance becomes worse, they often have a few more months or years in the (typically brighter) red channel in them.
    \item It is recommended to periodically image a bead sample to validate the PSF, as well as a Fluorescein bath to detect possible misalignment. For a detailed protocol, see Lees et al. \cite{Lees2024}.
    \item Be mindful of imaging artifacts. When suspecting an issue, go back to the basics, and isolate the error.
\end{itemize}
%
 For safety, it is good practice to shield the laser path. In addition to safety concerns, it will also help in keeping dust and dirt away from optical components.
\newpage

\section{Deriving the relationship between intensity and dispersion}
\textcolor{black}{We stated that the expected fluorescence $I(\varphi)$ as function of group delay dispersion $\varphi$ applied to a $\varphi_0$-dispersed Gaussian pulse of full-width-at-half-maximum $\Delta\tau$ can be written as
\begin{eqnarray}
    I(\varphi)=I_0 \left(1+16\log(2)^2\frac{(\varphi+\varphi_0)^2}{\Delta\tau^4}\right)^{-1/2}\label{main}.
\end{eqnarray}
To derive this expression, consider the electrical field of a Gaussian pulse of amplitude $E_0$, width $\Delta t$, center frequency $\omega_0$, phase $\Theta$, and centered at time $t=0$:
\begin{eqnarray}
E(t)=E_0\exp\left(-\frac{t^2}{4\Delta t^2}\right)\cdot\exp\left(-\complexi\left(\omega_0 t + \Theta\right)\right).
\end{eqnarray}
Its intensity is 
\begin{eqnarray}
P(t) = |E(t)|^2 = |E_0|^2 \exp\left(-\frac{t^2}{2\Delta t^2}\right)\label{intens}.
\end{eqnarray}
In the Fourier domain, the spectral content of this wave package is:
\begin{eqnarray}
\tilde{E}(\omega)=E_0\cdot\sqrt{2}\Delta t\, \exp\left(-\complexi\,\Theta -\Delta t^2(\omega - \omega_0)^2\right).
\end{eqnarray}
In the linear regime, frequency-dependent dispersion changes the electric field to
\begin{eqnarray}
\tilde{E}(\omega)\to\tilde{E}(\omega)\cdot\exp\left(\complexi\,\phi(\omega-\omega_0)\right)
\end{eqnarray}
with phase shift $\phi(\omega-\omega_0)$. We approximate this function to quadratic order $\phi(\omega-\omega_0)\approx a + b(\omega-\omega_0) + \frac{c}{2}(\omega-\omega_0)^2$. With this approximation, we obtain the Fourier representation of the electric field of the dispersed pulse:
\begin{eqnarray}
\tilde{E}^\text{disp}(\omega)=\tilde{E}(\omega)\cdot\exp\left(\complexi\,\left(a + b(\omega-\omega_0) + \frac{c}{2}(\omega-\omega_0)^2\right)\right).
\end{eqnarray}
Coefficient $a$ causes a phase shift and coefficient $b$ a time shift. Both do not change pulse width. Computing the inverse Fourier transform to obtain $E^\text{disp}(t)$ allows to compute the intensity of the dispersed pulse as 
\begin{eqnarray}
P^\text{disp}(t) = |E^\text{disp}(t)|^2 = |E_0|^2\frac{2\Delta t^2}{\sqrt{c^2 + 4\Delta t^4}}\exp\left(-\frac{2(b+t)^2\Delta t^2}{c^2+4\Delta t^4}\right)\label{intens_disp}.
\end{eqnarray}
Comparison with Eq. \eqref{intens} then shows that the pulse has broadened in time to $\Delta t\to \frac{\sqrt{c^2+4\Delta t^4}}{2\Delta t}$. Rewriting the widths of the dispersed pulse in the more common full-width-at-half-maximum $\Delta\tau$, using $\Delta t \to \Delta\tau/\sqrt{8\log(2)}$ for a Gaussian pulse, we obtain
\begin{eqnarray}
\Delta\tau^\text{disp} = \frac{\sqrt{\Delta\tau^4 + 16\log(2)^2c^2}}{2 \Delta\tau\sqrt{\log(4)}}.
\end{eqnarray}
The two-photon fluorescence intensity $I$ is proportional to the inverse of the pulse width, and the group delay dispersion is composed of the original dispersion $\varphi_0$ and the applied correction $\varphi$, so that $c \to \varphi_0 + \varphi$. We obtain
\begin{eqnarray}
I(\varphi) \propto \frac{1}{\Delta\tau^\text{disp}} = \frac{2 \Delta\tau\sqrt{\log(4)}}{\sqrt{\Delta\tau^4 + 16\log(2)^2(\varphi_0 + \varphi)^2}} = \frac{2\sqrt{\log(4)}}{\Delta\tau}\frac{1}{\sqrt{1 + 16\log(2)^2\frac{(\varphi_0 + \varphi)^2}{\Delta\tau^4}}}.
\end{eqnarray}
Absorbing the constants $\frac{2\sqrt{\log(4)}}{\Delta\tau}\to I_0$ yields Eq.~\eqref{main}. The same result for pulse broadening, with $16\log(2)^2\approx 7.68\dots$, is stated as Eq.~(3) in \cite{Zipfel2003}.
}

\nolinenumbers

\begin{thebibliography}{10}

\bibitem{Thorlabs}
Two Steering Mirrors Can be Used to Walk a Laser Beam to a New Path. Thorlabs 2024. 
\url{https://www.thorlabs.com/newgrouppage9.cfm?objectgroup_id=14221} and \url{https://www.youtube.com/watch?v=qzxILY6nOmA}

\bibitem{Conoptics2018}
Pockels Cell Concepts. Conoptics 2018.
\url{https://www.conoptics.com/wp-content/uploads/2018/06/SI2018-PockelsCellConcepts-190618-0009-18094.pdf}

\bibitem{Scientifica2024}
\#LabHacks: Aligning your Pockels cell for two-photon imaging. Scientifica 2024.
\url{https://www.scientifica.uk.com/neurowire/labhacks-aligning-your-pockels-cell-for-two-photon-imaging}

\bibitem{Vidrio2022}
Online documentation of ScanImage. Vidrio 2024. \url{https://docs.scanimage.org/index.html}

\bibitem{Pologruto2003}
Pologruto TA, Sabatini BL, Svoboda K. ScanImage: Flexible software for operating laser scanning microscopes. BioMed Eng OnLine 2, 13 (2003). \url{https://doi.org/10.1186/1475-925X-2-13}

\bibitem{Yao2023}
Yao P, Liu R, Broggini T, Thunemann M, Kleinfeld D. Construction and use of an adaptive optics two-photon microscope with direct wavefront sensing. Nat Protoc. 2023 Dec;18(12):3732-3766. doi: 10.1038/s41596-023-00893-w. Epub 2023 Nov 1. PMID: 37914781; PMCID: PMC11033548.

\bibitem{Hamamatsu2024}
Technical note on the Photomultiplier Tube Modules Series
H16200/H16201/H16204, Hamamatsu Photonics 2014 \url{https://www.hamamatsu.com/eu/en/product/optical-sensors/pmt/pmt-module/current-output-type/H16201-40.html}

\bibitem{Lees2024}
Lees RM, Bianco IH, Campbell RAA, Orlova N, Peterka DS, Pichler B, Smith SL, Yatsenko D, Yu CH, Packer AM. Standardised Measurements for Monitoring and Comparing Multiphoton Microscope Systems. bioRxiv [Preprint]. 2024 Jan 23:2024.01.23.576417. doi: 10.1101/2024.01.23.576417. PMID: 38328224; PMCID: PMC10849699.

\bibitem{Zipfel2003}
Zipfel WR, Williams RM, Webb WW. Nonlinear magic: multiphoton microscopy in the biosciences. Nat Biotechnol. 2003 Nov;21(11):1369-77. doi: 10.1038/nbt899. PMID: 14595365.

\end{thebibliography}

\end{document}

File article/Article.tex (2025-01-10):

% Template for PLoS
% Version 3.5 March 2018

\documentclass[10pt,letterpaper]{article}
\usepackage[top=0.85in,left=2.75in,footskip=0.75in]{geometry}

% amsmath and amssymb packages, useful for mathematical formulas and symbols
\usepackage{amsmath,amssymb}
\usepackage{changepage}
\usepackage[utf8x]{inputenc}
\usepackage{textcomp,marvosym}
\usepackage{cite}
\usepackage{nameref,hyperref}
\usepackage[right]{lineno}
\usepackage{microtype}
\DisableLigatures[f]{encoding = *, family = * }
\usepackage[table]{xcolor}
\usepackage{array}
\newcolumntype{+}{!{\vrule width 2pt}}

\usepackage{figchild}

% create \thickcline for thick horizontal lines of variable length
\newlength\savedwidth
\newcommand\thickcline[1]{%
  \noalign{\global\savedwidth\arrayrulewidth\global\arrayrulewidth 2pt}%
  \cline{#1}%
  \noalign{\vskip\arrayrulewidth}%
  \noalign{\global\arrayrulewidth\savedwidth}%
}

% \thickhline command for thick horizontal lines that span the table
\newcommand\thickhline{\noalign{\global\savedwidtch\arrayrulewidth\global\arrayrulewidth 2pt}%
\hline
\noalign{\global\arrayrulewidth\savedwidth}}

% Text layout
\raggedright
\setlength{\parindent}{0.5cm}
\textwidth 5.25in 
\textheight 8.75in

\usepackage[aboveskip=1pt,labelfont=bf,labelsep=period,justification=raggedright,singlelinecheck=off]{caption}

\bibliographystyle{plos2015}
\makeatletter
\renewcommand{\@biblabel}[1]{\quad#1.}
\makeatother

\usepackage{lastpage,fancyhdr,graphicx}
\usepackage{epstopdf}
\pagestyle{fancy}

\fancyhf{}
\rfoot{\thepage/\pageref{LastPage}}
\renewcommand{\headrulewidth}{0pt}
\renewcommand{\footrule}{\hrule height 2pt \vspace{2mm}}
\fancyheadoffset[L]{2.25in}
\fancyfootoffset[L]{2.25in}
\lfoot{\today}

%% Include all macros below
\newcommand{\microns}{~\textmu m~} % ALL UNITS UPRIGHT WITH SPACE
\newcommand{\invivo}{\textit{in vivo}~}
%% END MACROS SECTION

\begin{document}
\vspace*{0.2in}

% Title must be 250 characters or less.
\begin{flushleft}
{\Large
\textbf\newline{TWINKLE: An open-source two-photon microscope for teaching and research}
}
\newline
% Insert author names, affiliations and corresponding author email (do not include titles, positions, or degrees).
\\
Manuel Schottdorf\textsuperscript{1,2*}, % 0000-0002-5468-4255
P. Dylan Rich\textsuperscript{1}, % 0000-0001-9782-7984
E. Mika Diamanti\textsuperscript{1}, % 0000-0003-1199-3362
Albert Lin\textsuperscript{1,3}, % 0000-0002-4541-5889
Sina Tafazoli\textsuperscript{1}, % 0000-0003-1926-0227
Edward H. Nieh\textsuperscript{1,4}, % 0000-0003-2154-6224
Stephan Y. Thiberge\textsuperscript{1,5*} % 0000-0002-6583-6613
\\
\bigskip
\textbf{1} Princeton Neuroscience Institute, Princeton University, Princeton, NJ, USA\\
\textbf{2} Psychological and Brain Sciences, University of Delaware, Newark, DE, USA\\
\textbf{3} Center for the Physics of Biological Function, Princeton University, Princeton, NJ, USA\\
\textbf{4} Department of Pharmacology, School of Medicine, University of Virginia, Charlottesville, VA, USA \\
\textbf{5} Bezos Center for Neural Circuit Dynamics, Princeton University, Princeton, NJ, USA\\
\bigskip

% Use the asterisk to denote corresponding authorship and provide email address in note below.
* maschott@udel.edu\\
* thiberge@princeton.edu

\end{flushleft}
% Please keep the abstract below 300 words
\section*{Abstract}
Many laboratories use two-photon microscopy through commercial suppliers, or homemade designs of considerable complexity. The integrated nature of these systems complicates customization, troubleshooting, and \textcolor{black}{training on the} principles of two-photon microscopy. Here, we present ``Twinkle'': a microscope for Two-photon Imaging in Neuroscience, and Kit for Learning and Education. It is a fully open, high performing and \textcolor{black}{easy-to-set-up microscope that can effectively be used for both education and research}. The instrument features \textcolor{black}{a $>1\text{ mm}$ field of view}, using a modern objective with \textcolor{black}{3 mm} working distance and \textcolor{black}{2 inch diameter optics combined with GaAsP photomultiplier tubes} to maximize the fluorescence signal. We document our experiences using this system as a teaching tool in several two week long workshops, exemplify scientific use cases, and conclude with a broader note on the place of our work in the growing space of open scientific instrumentation.

\linenumbers

\section*{Introduction}
%
Two-photon microscopy\cite{Denk1990, Svoboda1997} \textcolor{black}{is a key technology across the modern life sciences\cite{Zipfel2003}, for example, in physiology\cite{Ueki2020, Dunn2002}, cancer research \cite{Perry2012}, plant biology \cite{Cheung2010}, and neuroscience\cite{So2000, Helmchen2005}. New scientific use cases and technological improvements are produced at a remarkable rate\cite{Luu2024}.} However, these instruments \textcolor{black}{are often published without detailed building instructions and explanations}. This suggests the need for an \textcolor{black}{easy-to-set-up microscope, at reasonable cost, that can be effectively used for education, dissemination, methods development and research.} We developed a high-performance and cost-effective two-photon microscope that can \textcolor{black}{easily be produced} in many neuroscience laboratories. Reflecting its use for ``\textbf{TW}o-photon \textbf{I}maging in \textbf{N}euroscience, and \textbf{K}it for \textbf{L}earning and \textbf{E}ducation'', we chose the acronym Twinkle. In this article, we share our design, document the performance of the system, explore possible research applications, and report our experiences collected during several teaching workshops. \textcolor{black}{Complete CAD drawings, bill of materials, optics simulations, and detailed building instructions are provided in the supplement.}

\section*{Materials and methods}
In two-photon laser-scanning microscopy\cite{Denk1990}, laser light is focused to a small excitation volume,  the ``focal point'', which is moved across the sample by the intermediary of resonant and galvanometric scanning mirrors. As the focal point probes different locations, different quantities of fluorescence light are produced by the sample. \textcolor{black}{This light is collected by a sensitive detector in the form of an electronically measurable photocurrent.} An image is then formed, mapping the detector photocurrent values to the locations of excitation volume: low and high photocurrents, respectively, becoming dark and bright pixels. Central to two-photon fluorescence excitation is the light source: a femtosecond-pulsed infrared laser of sufficient pulse energy to achieve, when focused by an objective lens, a photon density high enough for simultaneous absorption of two photons by a fluorescent molecule. Here, we design an open and high-performing microscope that uses these principles. As such, we have made all optical and mechanical designs, electronics, bill of materials (BOM), CAD assembly, testing results, and relevant schematics open to the public. \textcolor{black}{Excluding laser and optical table, the cost is around US-\$ 110k (2024). Including laser and table, the cost is around US-\$ 200k (2024).} A narrative of the design and the high-level view is presented here. For further details, we refer the reader to \nameref{S1_Appendix}. All code, figures and text, CAD designs, optics simulations, and BOM are available on  \url{https://github.com/BrainCOGS/Microscope} \textcolor{black}{and on Zenodo \cite{Zenodo2024}.}

\subsection*{Design specifications}
We aimed for a mechanical and optical assembly using as many off-the-shelf components as possible, with only few custom aluminium parts that can be machined in any university machine shop. Our design  facilitates the adaptation for \invivo imaging by providing a large space for the organism and ancillary hardware. Our system is made cost-effective, in part, by the availability of femtosecond laser systems based on fiber technology. Operating at a fixed wavelength, these systems come at the fraction of the cost of a tunable Ti:Sapphire laser \cite{Bueno2019}.\newline
More specifically, we aimed for (1) $\gtrapprox20\text{ cm}$ of free space around the objective in all directions to aid integration of the microscope with various peripheral equipment such as behavior boxes or a sample stage, and (2) imaging on a  $\approx 700\times 700\text{ \textmu m}^2$ minimum size field of view which is typical for imaging brain tissue at cellular resolution. (3) Compared to earliest open designs\cite{Rosenegger2014, Mayrhofer2015}, our system can make use of the large Numerical Aperture (NA) of  modern long-working-distance objectives to collect more fluorescence, but requires to adapt our design to their larger back apertures \cite{Janelia2024}.\newline
An overview of the microscope is shown in Fig.~\ref{fig1}. Fig.~\ref{fig1}A,B shows the system as a cartoon. Full details will be provided below. In short, we chose a 920 nm femtosecond pulsed laser, whose beam diameter is extended by a $2\times$ magnification telescope, before it reaches the scanning mirrors. The scanning mirrors are purchased as a mount-assembled set. Located as close as possible to each other, as we will see in the alignment procedure, neither of them can be exactly positioned in the focal plane of the scan lens. The choice of mounted scanners simplifies the design and construction, but leads to optical distortions across the field of view. \textcolor{black}{We found that this distortion does not exceed 5\% in our design (see below)}. The combined scan and tube lenses magnify the beam further to fill the objective's back aperture. Fluorescence from the specimen is then collected and brought to the aperture of two GaAsP photomultiplier tubes with suitable color filters. Fig.~\ref{fig1}C shows the CAD design of the entire assembly with important parts of the optical path labeled. Fig.~\ref{fig1}D shows an annotated picture of the microscope head. Notice that compared to the cartoon in Fig.~\ref{fig1}A,B, the optical path is folded with several mirrors. These mirrors make the microscope assembly more compact.

\begin{figure}[!t]
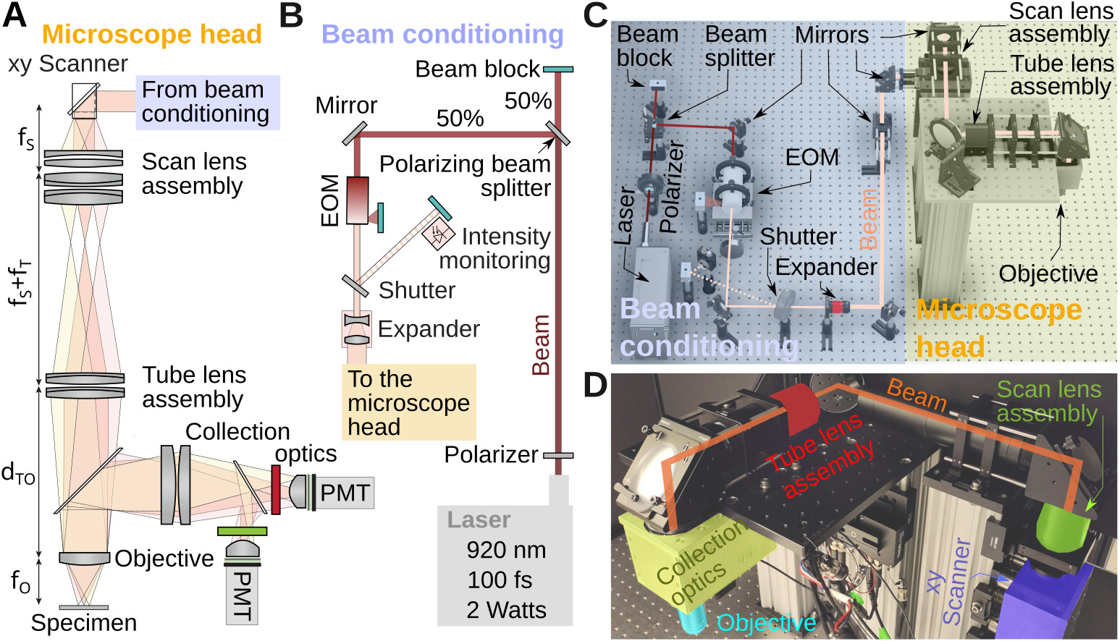
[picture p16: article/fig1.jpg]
    
    \caption{{\bf System overview.} \textbf{A)} \textcolor{black}{Key components of the microscope head. Shaded colors illustrate beam deflection angles. \textbf{B)} Cartoon of the beam conditioning components. First the beam is split by 50\%, the intensity adjusted with an electro-optic modulator (EOM) and the beam width with a telescope before entering the microscope head. \textbf{C)} 3D drawing of the full microscope, highlighting beam conditioning subsystem (blue) and the microscope head (yellow). For scale, the spacing between two holes on the optical table is 1 inch or 2.5 cm. \textbf{D)} Photograph of the microscope head with key elements labeled. This section is visible in panel A.}}
    \label{fig1}
\end{figure}

\subsection*{Assembly on the table}
Various components are used between the laser and the microscope head to condition the beam, and  for intensity control, Fig.~\ref{fig1}B. Out of the laser head, the beam first encounters a waveplate (AHWP10M-980, Thorlabs). This is a birefringent crystal that can rotate the linear polarization of the laser to any angle. Next, the beam travels through a polarizing beamsplitter cube (PBS103, Thorlabs). This splits the beam into two orthogonal polarization components whose relative intensity is adjusted by the orientation of the waveplate. We set the orientation of the waveplate to split the beam into equal power components, the second one being eventually used for a second microscope installed on the other extremity of the table. In the cartoon, this second beam is sent to a beam block (LB1, Thorlabs). \textcolor{black}{We want to stress that this beam-splitting hardware is optional. However, modern lasers have enough power to supply two microscopes at the same time. It is therefore often strategic to split the beam into two beams, with half of the intensity each, to allow one laser (the most expensive component) to power two systems.} Next, the beam passes through an electro-optic modulator (EOM), a Pockels cell (350-80-LA-02, Conoptics). This device allows rapid and electronic control of the laser's power level. It uses a crystal whose refractive index is controlled by an external electric field, combined with a polarizer. This can be thought of as a voltage-controlled wave plate, in which the electric field controls how much light travels through the polarizer. Next, the beam travels through an open mechanical 6 mm diameter shutter (LS6S2ZM1, Vincent Associates). When closed, the laser reflected on the shutter reflective blades is sent to another beam block. Beam blocks are not perfect absorber, so we can use advantageously the weak back scattered light from the beam block to calibrate the Pockels cell. In our set-up, a photodiode (PDA36A2, Thorlabs) is thus facing the beam block. Following the shutter, the beam travels though a $2\times$ telescope (GBE02-B, Thorlabs) doubling its diameter. Past the telescope, the beam is then reflected off several mirrors in a periscope configuration before entering a custom aluminium box housing, mounted to a 95 mm optical rail (XT95 series, Thorlabs), that houses the two scanning mirrors (CRS8K/6215H scanning mirror set, Novanta), shown in blue in Fig.~\ref{fig1}D. Leaving the scanners, the beam then travels first through the scan lens (green) and tube lens (red), passes through the long pass dichroic mirror of the collection box assembly (yellow) and finally the objective (cyan). The design of these components is covered in the next paragraphs. The steering mirrors in our system are all P01 silver protected mirrors from Thorlabs. Silver mirrors contribute minimally to dispersion which is inevitable when light travels through various optical components. Limiting the dispersion makes it possible to correct for it with the laser's built-in dispersion compensation.
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

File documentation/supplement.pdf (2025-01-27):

## Supplemental Online Material

This supplemental material to the article “TWINKLE: An open-source two-photon microscope for teaching and research” describes the assembly, function and alignment of all parts of the microscope. Technical specifications are provided through the CAD files and the Zemax simulations in the online repository at https://github.com/BrainCOGS/Microscope.

## Contents

1 Preface | 2
2 Assembly on the optical table | 4
3 Last steps | 13
4 Assembly of subcomponents | 14
5 Software and control | 24
6 Recommendations for use | 28
7 Deriving the relationship between intensity and dispersion | 29
January 27, 2025 | 1/30

1 | Preface | 1
1.1 | Safety | 2
Class 4 lasers are extremely dangerous. A reflection on a surface can be enough to | 3
inflict permanent eye damage. Safety protocols must be observed. Consult with your | 4
institution’s environmental health and safety officer and take proper training before | 5
performing any work with a laser system. Learn from people experienced with these | 6
devices and work carefully. | 7
During alignment, always wear goggles (ours were ML1 by NoIR LaserShields with an | 8
optical density > 7 in the relevant range around 920 nm), remove jewelry and watches, | 9
only use non-reflective tools, do not store unnecessary items on the optical table, and | 10
use the low laser power (“alignment mode”) whenever possible. Once the assembly | 11
progresses further, full power mode is necessary. Extra care must be taken then. Always | 12
use Laser Viewing Cards to track the laser. We use Thorlabs VRC4. Always be | 13
conscious where the beam is, and where the beam goes. The beam must be terminated | 14
in beam blockers and should be shielded whenever possible with opaque plastic or | 15
anodized aluminium tubes to increase safety. | 16
1.2 | Miscellaneous tools and tips | 17
The following tools are used throughout the build process: | 18
- A high quality duster to remove any residue from optical surfaces. We use a | 19
| Miller-Stephenson Aero-Duster Ultra MS-222L, in addition to lens tissues (MC-5, | 20
| Thorlabs) and Methanol (Sigma-Aldrich). | 21
- To glue optical filters we used an extra fast setting epoxy (Hardman | 22
| Double/Bubble Epoxy). To seal small gaps, we use black silicone putty (V-tie | 23
| self-setting silicone rubber). | 24
- We used either McMaster or Thorlabs screwdrivers and hex keys. | 25
- For alignment, we used laser viewing cards (VRC4, Thorlabs), cage system | 26
| alignment plates (VRC4CPT, Thorlabs), and irises (SM1 Graduated | 27
| Ring-Actuated Iris Diaphragm, SM1D12C, Thorlabs). | 28
The following general tips might be of help as well: | 29
- Shield the beam as soon as alignment of a particular section is done. This | 30
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

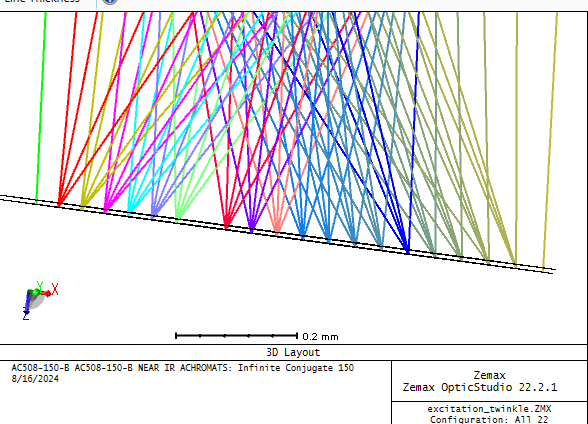
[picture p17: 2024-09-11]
zemax/Excitation/3DLayout_angle.png

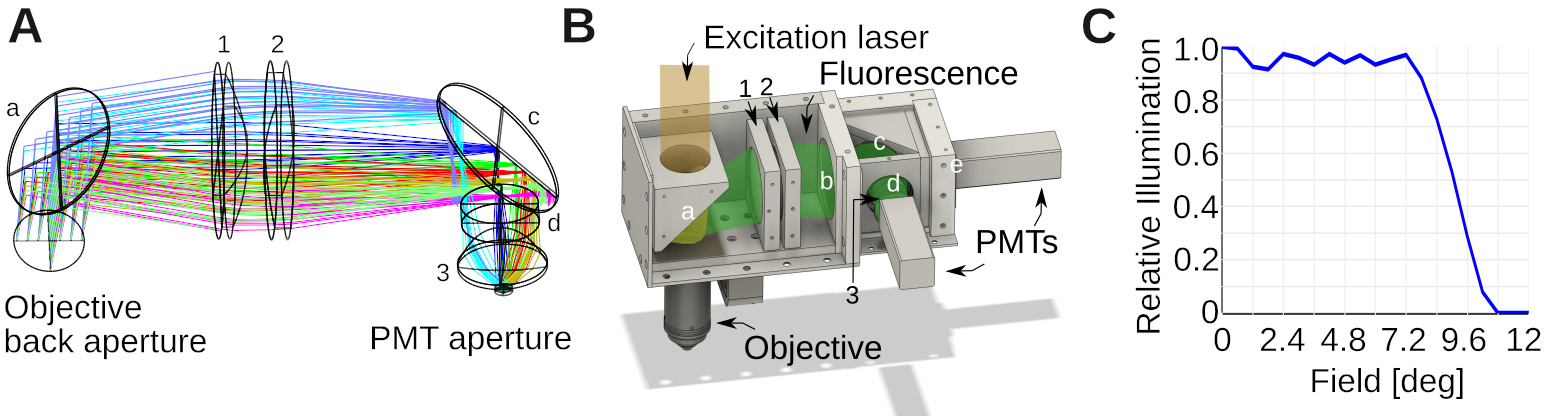
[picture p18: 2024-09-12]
article/fig3.jpg

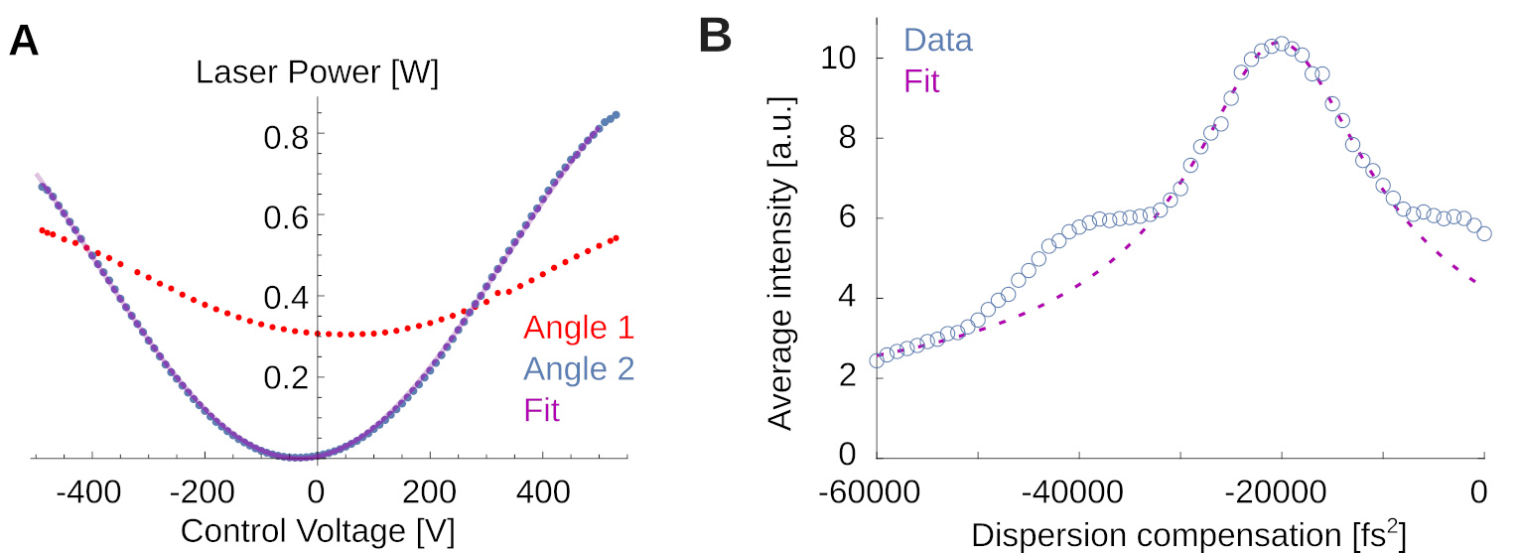
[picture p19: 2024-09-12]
article/fig9.jpg

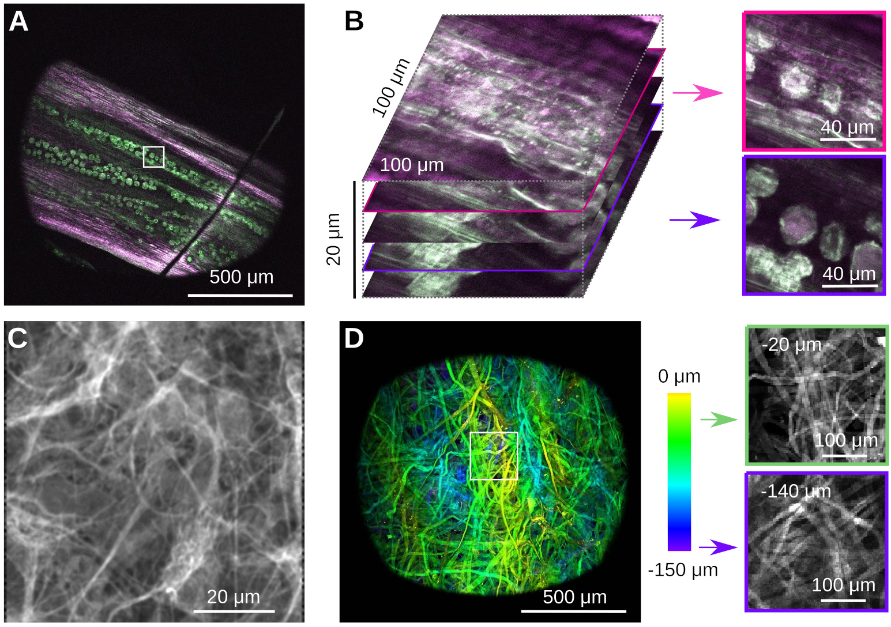
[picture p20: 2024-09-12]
article/fig6.jpg

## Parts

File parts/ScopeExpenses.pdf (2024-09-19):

Item Name | Product Details | Web link | Cost | Quantity | Notes

Beam Conditioning
Ultra-compact femtosecond laser | Spark laser ALCOR 920nm 2W | https://rpmclasers.com/wp-content/uploads/products/ALCOR%20920.pdf?srsltid=AfmBOopx5II4QLZOXl_lS5Hx6BuiWs9P8b4oDAZp8-PJh-laY7jA7NLh $71,200 | | 1
Ultra-compact femtosecond laser | Extended warranty | | $19,936 | 1
Beam block | LB1/M - Beam Block, 400 nm - 2 µm, | https://www.thorlabs.de/thorproduct.cfm?partnumber=LB1/M | $59 | 2
Adjustible ring mount | Edmund Optics (#36-605) | https://www.edmundoptics.com/p/95mm-outer-diameter-three-screw-adjustable-ring-mount/4203/ $76 | | 2
Beam block | LB2 - Beam Block, 1 - 12 µm, | https://www.thorlabs.de/thorproduct.cfm?partnumber=LB2 | $181 | 3
IR detector card | VRC4 - 790 - 840 nm, 870 - 1070 nm, 1500 - 1590 nm | https://www.thorlabs.com/thorproduct.cfm?partnumber=VRC4 | $94 | 1
Cage alignment plate | VRC4CPT | https://www.thorlabs.com/thorproduct.cfm?partnumber=VRC4CPT#ad-image-0 $36 | | 1
Iris | SM1D12C | https://www.thorlabs.com/thorproduct.cfm?partnumber=SM1D12C#ad-image-0 $120 | | 3
Cage plate | CP33 | https://www.thorlabs.com/thorproduct.cfm?partnumber=CP33 | $19 | 1
Mounted achromatic half-wave plate | AHWP10M-980 - Ø1" | https://www.thorlabs.com/thorproduct.cfm?partnumber=AHWP10M-980$1,059 | | 1
Rotation mount | PRM1 | https://www.thorlabs.com/thorproduct.cfm?partnumber=PRM1 | $325 | 1
Polarizing beamsplitter cube | PBS103 - 10 mm | https://www.thorlabs.com/thorproduct.cfm?partnumber=PBS103 | $222 | 1
Kinematic platform mount | KM100B - 1.92" x 1.92" | https://www.thorlabs.com/thorproduct.cfm?partnumber=KM100B | $66 | 1
Adjustable clamping arm | PM4 | https://www.thorlabs.com/thorproduct.cfm?partnumber=PM4 | $27 | 1
Laser power meter | Coherent FieldMaxII | https://coherentinc.my.site.com/Coherent/laser-measurement/power-energy-meters/1098579?cclcl=en_US $1,283 | | 1
Mirror | PF10-03-P01 | https://www.thorlabs.com/thorproduct.cfm?partnumber=PF10-03-P01 | $56 | 5
Mirror mount | KM100 | https://www.thorlabs.com/thorproduct.cfm?partnumber=KM100#ad-image-0$42 | | 5
Aligment tool 103 | Conoptics | refer to https://conoptics.com/wp-content/uploads/2013/09/Conoptics_Modulator_Alignment_Procedure.pdf 1
Si switchable gain detector | PDA36A2 - Si Switchable Gain Detector, 350 - 1100 nm | https://www.thorlabs.com/thorproduct.cfm?partnumber=PDA36A2 | $374 | 1
Shutter | LS6S2ZM1 Vincent Associates | https://www.uniblitz.com/products/ls6/ | $1,045 | 1
Shutter driver | VCMD1 | https://www.uniblitz.com/products/vcm-d1-shutter-driver/ | $1,210 | 1
Long pass filter | FELH0850 - Ø25.0 mm Longpass Filter, Cut-On Wavelength: 850 nm https://www.thorlabs.com/thorproduct.cfm?partnumber=FELH0850 | | $144 | 1
Conoptics Pockels cell 101 alignment tool | Model 102A Adj. Modulator Mount with Model 103 Alignment | https://www.conoptics.com/conoptics-accessories/model-102-adjustable-mount-with-isolator/ $950 | | 1
Beam expander (Telescope) | GBE02-B - 2X Achromatic Galilean Beam Expander, | https://www.thorlabs.com/thorproduct.cfm?partnumber=GBE02-B | $479 | 1
Right-angle kinematic mirror mount | KCB1 | https://www.thorlabs.com/thorproduct.cfm?partnumber=KCB1#ad-image-0$155 | | 1
Cage plate | CP12 - 30 mm Cage Plate, Ø1.2" Double Bore for SM1 and C-Mount Lens Tubes https://www.thorlabs.com/thorproduct.cfm?partnumber=CP36 | | $24 | 1
Broadband precision window | WG11010 - Ø1" N-BK7 Broadband Precision Window, Uncoated, t = 1 mm https://www.thorlabs.com/thorproduct.cfm?partnumber=WG11010 | | $91 | 2
Thread depth | SM1L20 - SM1 Lens Tube, 2.00" Thread Depth, One Retaining Ring Included https://thorlabs.com/thorproduct.cfm?partnumber=SM1L20 | | $18 | 1
Drop-on rail carriage | XT95RC4 - Drop-On Rail Carriage for 95 mm Rails, 4.00" Long, 1/4"-20 Tapped Holes https://www.thorlabs.com/thorproduct.cfm?partnumber=XT95RC4 | | $143 | 1
Mirror mount with smooth cage rod bores | KCB2EC | https://www.thorlabs.com/thorproduct.cfm?partnumber=KCB2EC | $268 | 1
Tube holder | LPC01 | https://www.thorlabs.com/thorproduct.cfm?partnumber=LCP34 | $45 | 1
Cage assembly Rod | ER6-P4 | https://www.thorlabs.com/thorproduct.cfm?partnumber=ER6-P4 | $36 | 3
Table clamp | XE25CL2 | https://www.thorlabs.com/thorproduct.cfm?partnumber=XE25CL2 | $14 | 10
Slip-on lens tube cover | SC1L24 | https://www.thorlabs.com/thorproduct.cfm?partnumber=SC1L24 | $11 | 1
Slip-on lens tube cover | SC600 | https://www.thorlabs.com/thorproduct.cfm?partnumber=SC600 | $40 | 1
Post holder | PH3-P5 - Ø1/2"(Pack of 5) | https://www.thorlabs.com/thorproduct.cfm?partnumber=PH3-P5#ad-image-0$46 | | 5
Optical post | TR3-P5(Pack of 5) | https://www.thorlabs.com/thorproduct.cfm?partnumber=TR3-P5 | $28 | 2
Broadband windows | WG11010-B - Ø1" N-BK7 Broadband Precision Window, AR Coated: 650 - 1050 nm, t = 1 mm https://www.thorlabs.com/thorproduct.cfm?partnumber=WG11010-B | | $103 | 2
Adapter with external SM1 threads and internal SM2 threads | SM1A2 | https://www.thorlabs.com/thorproduct.cfm?partnumber=SM1A2 | $28 | 1
Cage plate | CP08 | https://www.thorlabs.com/thorproduct.cfm?partnumber=CP08 | $23 | 1
Scanning mirror set | 6SD11502, Novanta | Quote | $5,600 | 1
Pockels cell | Model 302RM Driver | Quote | $5,725 | 1
Pockels cell | Model 350-80-LA-02 KD*P Series E-O Modulator for use in the NIR Quote | | $5,500 | 1
Pockels cell | BK Option used to min. piezo-electric resonances for Model 350 Series Quote | | $850 | 1
Pockels cell | Model 103 Alignement Tool | Quote | $75 | 1

Item Name | Product Details | Web link | Cost | Quantity | Notes

Lens Assemblies
Aero-Duster | CA4-US | https://www.thorlabs.com/thorproduct.cfm?partnumber=CA4-US | $26 | 2
Lens Tube Spacer | SM1S20 - SM1 Lens Tube Spacer, 2" Long | https://www.thorlabs.com/thorproduct.cfm?partnumber=SM1S20 | $17 | 1
Andustble lens tube | SM2V05 | https://www.thorlabs.com/thorproduct.cfm?partnumber=SM2V05 | $55 | 1
Lens Tubes | SM2L10 | https://www.thorlabs.com/newgrouppage9.cfm?objectgroup_id=3383 | $35 | 3
Lens Tubes | SM2L30 | https://www.thorlabs.com/newgrouppage9.cfm?objectgroup_id=3383 | $35 | 2
Lens Tubes | SM2L05 | https://www.thorlabs.com/newgrouppage9.cfm?objectgroup_id=3383 | $35 | 1
Lens Tubes | SM2L15 | https://www.thorlabs.com/newgrouppage9.cfm?objectgroup_id=3383 | $35 | 1
Lens Tubes | SM2L20 | https://www.thorlabs.com/newgrouppage9.cfm?objectgroup_id=3383 | $35 | 1
Lens Tubes | SM1L15 | https://www.thorlabs.com/newgrouppage9.cfm?objectgroup_id=3307 | $17 | 2
Lens Tubes | SM1L20 | https://www.thorlabs.com/newgrouppage9.cfm?objectgroup_id=3307 | $18 | 4
Spanner Wrench | SPW604 - Spanner Wrench for SM2-Threaded Retaining Rings, Length = 4.35" https://www.thorlabs.com/thorproduct.cfm?partnumber=SPW604 | | $52 | 1
Optical lens excitation path | LB1199-B | https://www.thorlabs.com/thorproduct.cfm?partnumber=LB1199-B | $55 | 1
Optical lens excitation path | ACT508-200-B | https://www.thorlabs.com/thorproduct.cfm?partnumber=ACT508-200-B $157 | | 2
Optical lens excitation path | ACT508-750-B | https://www.thorlabs.com/thorproduct.cfm?partnumber=ACT508-750-B $157 | | 2
Optical lens emission path | LA1384-A | https://www.thorlabs.com/thorproduct.cfm?partnumber=LA1384-A | $46 | 1
Optical lens emission path | LB1607-A | https://www.thorlabs.com/thorproduct.cfm?partnumber=LB1607-A | $55 | 1
Optical lens emission path | ACL25416U-A | https://www.thorlabs.com/thorproduct.cfm?partnumber=ACL25416U-A | $32 | 2
Optical lens excitation path | KPC070AR.16 | https://www.newport.com/p/KPC070AR.16 | $104 | 1

Item Name | Product Details | Web link | Cost | Quantity | Notes

Microscope Head
Machine shop | Machining the microscope pieces | | $6,670 | 1
Black anodization of microscope parts | Hillock anodization | https://www.hillockanodizing.com/ | $500 | 1
Nikon 16X objective, and thread adapter | N16XLWD-PF - 16X Nikon CFI LWD Plan Fluorite Objective, 0.80 NA, 3.0 mm WD https://www.thorlabs.com/thorproduct.cfm?partnumber=N16XLWD-PF $7,824 | | | 1
Piezoelectric objective collar | P-725.xCDE1S PIFOC | https://www.pi-usa.us/en/products/more-products/nanopositioning-piezo-flexure-stages/pifoc-objective-pinano-sample-scanners-for-microscopy/p-725xcde1s-pifoc-scanner-system-for-microscope-objectives $16,021 | | 1
Silicon putty | TG-NSP50-1LB | https://www.digikey.com/en/products/detail/t-global-technology/TG-NSP50-1LB/13246097?utm_adgroup=&utm_source=google&utm_medium=cpc&utm_campaign=PMax%20Shopping_Product_Medium%20ROAS%20Categories&utm_term=&utm_content=&utm_id=go_cmp-20223376311_adg-_ad-__dev-c_ext-_prd-13246097_sig-Cj0KCQjwtsy1BhD7ARIsAHOi4xalIkKnn4X8kGJfYZQ-DaZbw4jGDBVh71qLlgcJA4r8u8By70HPzekaAolDEALw_wcB&gad_source=1&gclid=Cj0KCQjwtsy1BhD7ARIsAHOi4xalIkKnn4X8kGJfYZQ-DaZbw4jGDBVh71qLlgcJA4r8u8By70HPzekaAolDEALw_wcB $61 | | 1
Connection cable for PMT gain | | https://www.mouser.com/ProductDetail/Belden-Wire-Cable/8445-060100?qs=V3c4vtsS7n0oWQtUr0OZUA%3D%3D&mgh=1&utm_id=17222215321&gad_source=1&gclid=Cj0KCQjwtsy1BhD7ARIsAHOi4xbOnWFk-u-tHGWLPDHymgm_rdDJt3eCMPsa9AXdbyqerBtyYRLDr7waApTSEALw_wcB $242 | | 1
Cable connector | Neutrik NC4MX | https://www.markertek.com/product/nc4mx/neutrik-nc4mx-4-pin-xlr-male-cable-connector $5 | | 2
Drop-on rail carriage | XT95RC2 | https://www.thorlabs.com/thorproduct.cfm?partnumber=XT95RC2 | $101 | 3
Drop-on rail carriage | XT95RC3 | https://www.thorlabs.com/thorproduct.cfm?partnumber=XT95RC3 | $122 | 1
Aluminum breadboard | MB12 | https://www.thorlabs.com/thorproduct.cfm?partnumber=MB12 | $172 | 1
Mounting base | BA2 | https://www.thorlabs.com/thorproduct.cfm?partnumber=BA2#ad-image-0 | $8 | 4
Mounting base | BA1 | https://www.thorlabs.com/thorproduct.cfm?partnumber=BA1#ad-image-0 | $6 | 5
Mounting base | BA1S | https://www.thorlabs.com/thorproduct.cfm?partnumber=BA1S#ad-image-0 $6 | | 5
Cage plate | CP02/M | https://www.thorlabs.com/thorproduct.cfm?partnumber=CP33/M | $20 | 1
Angle bracket | Angle Bracket, 90°, 1/4-20 (M6) Slots, 1 in. Spacing 360-90 | https://www.newport.com/p/360-90 | $100 | 1
Hardman Double/Bubble Epoxy | | https://www.amazon.com/Hardman-Double-Bubble-Setting-minute/dp/B013WHZFSY/ref=asc_df_B013WHZFSY/?tag=hyprod-20&linkCode=df0&hvadid=692875362841&hvpos=&hvnetw=g&hvrand=7417696031901901692&hvpone=&hvptwo=&hvqmt=&hvdev=c&hvdvcmdl=&hvlocint=&hvlocphy=9007308&hvtargid=pla-2281435179818&psc=1&mcid=3c127bc7621834718028b37434c250fb&hvocijid=7417696031901901692-B013WHZFSY-&hvexpln=73 $18 | | 1
Photomultiplier tube module(PMT) | Hamamatsu H16201-40 | https://www.hamamatsu.com/eu/en/product/optical-sensors/pmt/pmt-module/current-output-type/H16201-40.html $4,355 | | 2
PMT transimpedance amplifier | TIA60 | https://www.thorlabs.com/thorproduct.cfm?partnumber=TIA60 | $1,151 | 2
Single band band-pass filter | FF01-525/45-32, AVR Optics | Quote | $582 | 1
Single band band-pass filter | FF01-600/52-32, AVR Optics | Quote | $582 | 1
Dichroic beamsplitter | FF562-DI03-40X52, AVR Optics | Quote | $812 | 1
680 nm blocking short-pass filter | FF01-680/SP-50, AVR Optics | Quote | $5,760 | 1
Dichroic beamsplitter | FF665-DI02-40X55, AVR Optics | Quote | $1,766 | 1
Screws | 4-40 X 5/16 Socket Cap Screw Stainless Steel | https://www.mfsupply.com/Socket-Head-Cap-Screws-p/sc4cx5-fslash-16ssd.htm $19 | | 1
Screws | 4-40 Stainless Steel Nylon-Tipped Setscrew, 1/8" Long | https://www.thorlabs.de/thorproduct.cfm?partnumber=SS4N013 | $15 | 1
Screws | 8-32 X 3/8 Socket Cap Screw Stainless Steel | https://www.mfsupply.com/Socket-Head-Cap-Screws-p/sc8cx3-fslash-8ssd.htm $25 | | 1
Screws | stainless steel socket head screw, 4-40 Thread Size, 3/4 inches long https://accu-components.com/us/imperial-cap-head-screws/28948-SSC-4-40-3-4-A2?google_shopping=1&c=2&gad_source=1&gclid=CjwKCAjw3P-2BhAEEiwA3yPhwDUp4Mx5Z2JknvpfJW9v1Gp1pUfNcTjy_uRBW5nDD3ZGPZ6_9Q-Q_BoCAz4QAvD_BwE $1 | | | 12
Screws | 4-40, undercut, 3/16 inch screws | https://www.amazon.com/Coarse-Thread-Machine-Phillips-Undercut/dp/B0CVFP1FNV?th=1 $21 | | 1
Screws | 4-40 5/16 inch, socket cap screws | https://www.amazon.com/Button-Socket-Screw-Allen-Thread/dp/B07N9WG9RF $11 | | 1
Screws | 8/32, 1/2 inch, socket cap screws | https://boltdepot.com/Product-Details?product=4999&qty=1&gad_source=1&gclid=CjwKCAjw3P-2BhAEEiwA3yPhwDDDiZnqwPfj8wwLWMw9zE9LCygfeB5W2xDiLMoJHfADUVr_cLNVahoCCSIQAvD_BwE $7 | | 1
Screws | 8/32, 3/8 inch, undercut screws | https://www.tannerbolt.com/8c37mfupz-8-32-x-3-8-undercut-machine-screws-undercut-flat-phillips-head-fully-threaded-zinc-plated $5 | | 1
Screws | 4-40 thread, 1/8 inch screws | https://accu-components.com/us/imperial-cap-head-screws/28939-SSC-4-40-1-8-A2?google_shopping=1&c=2&gad_source=1&gclid=CjwKCAjw3P-2BhAEEiwA3yPhwNuU39zWhU7-2pKC-0mu9-QRdgAVFRDrOHFqDba4xbJF8kPhOBq3GRoCX70QAvD_BwE $1 | | 12
Screws | 4-40, 1/2 inch, socket cap screws | https://boltdepot.com/Product-Details?product=4986&qty=1&gad_source=1&gclid=CjwKCAjw3P-2BhAEEiwA3yPhwEjma8rjGLYKXgjX2TVnf98RT_vjRCp1sykVsfH-1B1pMIX80MC4wBoCvnUQAvD_BwE $7 | | 1
Screws | Ultra low-profile hex socket cap screw | https://us.misumi-ec.com/vona2/detail/110302280540/?HissuCode=CBSTSR2-6 $4 | | 20
Wire | 28 AWG | https://www.digikey.com/en/products/detail/remington-industries/28STRPTFEKIT/11613948 $52 | | 1
Protected silver mirror | PF30-03-P01 - Ø3" Protected Silver Mirror | https://www.thorlabs.com/thorproduct.cfm?partnumber=PF30-03-P01 | $402 | 1
Precision kinematic mirror mount | KS3 | https://www.thorlabs.com/thorproduct.cfm?partnumber=KS3#ad-image-0$224 | | 1
Protected silver elliptical mirror | PFE20-P01 | https://www.thorlabs.com/thorproduct.cfm?partnumber=PFE20-P01 | $184 | 2
Retaining Ring | SM2RR | https://www.thorlabs.com/thorproduct.cfm?partnumber=SM2RR | $8 | 1

Item Name | Product Details | Web link | Cost | Quantity | Notes

Electronics
Multimeter | Fluke 117 | https://www.fluke.com/en-us/product/electrical-testing/digital-multimeters/fluke-117 $290 | | 1
Circuit enclosure box | EG6 | https://www.acopian.com/box-gb.html | $60 | 1
Banana Patch Cord | | https://www.thorlabs.com/thorproduct.cfm?partnumber=T13120 | $11 | 10
Coaxial Cable | 60" | https://www.thorlabs.com/thorproduct.cfm?partnumber=2249-C-60 | $22 | 15
Power supply | Instek GPD-3303D Power Supply, Triple Output, 2x 30 V / 3 A, 2.5-5 V / 3 A, 100 mV / 10 mA, GPD Series https://www.testequity.com/product/17670-2-GPD-3303D?gad_source=1&gclid=CjwKCAjw_Na1BhAlEiwAM-dm7PGohjh6-7kT4DuzRIFO7rQi2EHz2tHn9Y7Jyv_dG0aH2M9UKHq3zhoC_XYQAvD_BwE $379 | | | 1
Power supply | Keysight E3630A DC Linear Power Supply, Triple Output, 6 V / 2.5 A, 2x 20 V /.5 A, 35-50 W, E36xxA Series https://www.testequity.com/product/12379-1-E3630A?gad_source=1&gclid=CjwKCAjw_Na1BhAlEiwAM-dm7PwbuFzbbr8dIe4Wfam-tRWs-xiAQpw40n2488x6nmTV3sR0ibDAmxoCLb4QAvD_BwE $1,173 | | | 2
Digital panel meter | DMS-20PC-1-FM-C | https://www.tti.com/content/ttiinc/en/apps/part-detail.html?partsNumber=DMS-20PC-1-FM-C&mfgShortname=MPS&utm=ga-shop1&gad_source=1&gclid=CjwKCAjw_Na1BhAlEiwAM-dm7HDLXjRdnM9JZXPbVfPowWUQQbn2kjm5tfucu7yZ4Y5p77EpBLlTEBoClBEQAvD_BwE $65 | | 2
Potentiometer | 3500S-2-503L | https://www.digikey.com/en/products/detail/bourns-inc./3500S-2-503L/2534228?utm_adgroup=&utm_source=google&utm_medium=cpc&utm_campaign=PMax%20Shopping_Product_Low%20ROAS%20Categories&utm_term=&utm_content=&utm_id=go_cmp-20243063506_adg-_ad-__dev-c_ext-_prd-2534228_sig-CjwKCAjwufq2BhAmEiwAnZqw8mLuEqL2ZmZxYzLbm1ragSttZWo5BnyTf4xwWRQ3GZWKRlSeIrHhohoCA7QQAvD_BwE&gad_source=1&gclid=CjwKCAjwufq2BhAmEiwAnZqw8mLuEqL2ZmZxYzLbm1ragSttZWo5BnyTf4xwWRQ3GZWKRlSeIrHhohoCA7QQAvD_BwE $85 | | 2
Resistor | 12K | https://www.digikey.com/en/products/detail/yageo/MFR-25FTE52-12K/13921465?utm_adgroup=Yageo&utm_source=google&utm_medium=cpc&utm_campaign=PMax%20Shopping_Supplier_Yageo&utm_term=&utm_content=Yageo&utm_id=go_cmp-17816160916_adg-_ad-__dev-c_ext-_prd-13921465_sig-CjwKCAjwufq2BhAmEiwAnZqw8qZ3nG6K0Wj-f0ECR2YtulXqotXAJ3a-XChtWq5RDBDmMGW5gmilQBoC7nsQAvD_BwE&gad_source=1&gclid=CjwKCAjwufq2BhAmEiwAnZqw8qZ3nG6K0Wj-f0ECR2YtulXqotXAJ3a-XChtWq5RDBDmMGW5gmilQBoC7nsQAvD_BwE $1 | | 2
Toggle switch | ST141D00 | https://www.digikey.com/en/products/detail/e-switch/ST141D00/2116289?utm_adgroup=&utm_source=google&utm_medium=cpc&utm_campaign=PMax%20Shopping_Product_Low%20ROAS%20Categories&utm_term=&utm_content=&utm_id=go_cmp-20243063506_adg-_ad-__dev-c_ext-_prd-2116289_sig-CjwKCAjw3P-2BhAEEiwA3yPhwGmC6p_jJ3R-EOTrzL5VFQMQOK0wzO0JGQU2gz180qnOzyUWRP6LGBoCqfkQAvD_BwE&gad_source=1&gclid=CjwKCAjw3P-2BhAEEiwA3yPhwGmC6p_jJ3R-EOTrzL5VFQMQOK0wzO0JGQU2gz180qnOzyUWRP6LGBoCqfkQAvD_BwE $6 | | 2

Item Name | Product Details | Web link | Cost | Quantity | Notes

Computer & Control & Rack
vDAQ (DAQ system from Vidrio 16k) + Optimized PC for ScanImage (3.5k) + bundle discount (-1k) +shipping Vidrio technologies | | https://www.mbfbioscience.com/products/scanimage/ | $18,653 | 1
Rack Total (individual items below) | Jacobson-associates | Quote | $2,400 | 1
10 Series Vertical Frame | XFR-267019 | Quote | $857 | 1
Locking 350# Caster | HW-450-LK | Quote | $33 | 4
40U Mounting Rails | XMA-70 - Mounted on the Front | Quote | $87 | 1
40U Mounting Rails | XMA-70 - Mounted at B - 25.125" | Quote | $87 | 1
40U Mounting Straps | XMA-70 - Mounted at A - 20.062 | Quote | $85 | 1
48" Vertical PDU | WM-481015-PC | Quote | $125 | 1
13U Formed Steel Filler Panel - Solid | XPN-2219 | Quote | $74 | 1
2U Retractable Keyboard Tray | RKT-0319-S | Quote | $497 | 1
1U Heavy Duty Shelf - Solid | XES-2019 - Mounted in the Front Opening at U21 | MOUNT FRONT AT U21 Quote | | $68 | 1
1U Heavy Duty Shelf - Solid | XES-2019 - Mounted in the Front Opening at U22 | MOUNT FRONT AT U22 Quote | | $68 | 1
1U Heavy Duty Shelf - Solid | XES-2019 - Mounted in the Front Opening at U27 | MOUNT FRONT AT U27 Quote | | $68 | 1
Full Depth Bottom Panel - Solid | XBP-2619 | Quote | $82 | 1

Item Name | Product Details | Web link | Cost | Quantity | Notes

## Miscellaneous

Fluorescent beads | | https://www.bangslabs.com/product-selection/FSDG002 $244 | | 1
Low melting point agarose | YPD agar | https://www.sigmaaldrich.com/US/en/product/sial/y1500?utm_source=google%2Cgoogle&utm_medium=organicshopping%2Ccpc&utm_campaign=20790375250&utm_content=154400301983&gclid=CjwKCAjw_4S3BhAAEiwA_64YhkLk0S0pKYW24QlnTZBEMV-qi3uuLcn8EMNG9DP5yenXXQOjK1-gVhoCeX8QAvD_BwE $111 | | 1
Fluorescein | -MG-F | https://www.sigmaaldrich.com/US/en/product/sigma/46955?srsltid=AfmBOoo5I7CFSdrzJghs5oYKP5xRSfb5IdWRbJe9Ec4rzetyeq7BZbxX $36 | | 1
Cover slips | BI0094A | https://www.sigmaaldrich.com/US/en/product/eiscolabs/bi0094a $10 | | 1
Microscope slides | CLSX-EA | https://www.sigmaaldrich.com/US/en/product/aldrich/cls294875x25?utm_source=google%2Cgoogle&utm_medium=organicshopping%2Ccpc&utm_campaign=21043330280&utm_content=&gclid=CjwKCAjw_4S3BhAAEiwA_64Yhu81EgO0BPQEwl2ZpRHKvmhFp-Rj9Ac6p7OkfTJHJJColxpjlM0zqhoCvO4QAvD_BwE $35 | | 1
Calibration standard | R1L3S3 | https://www.thorlabs.com/thorproduct.cfm?partnumber=R1L3S3P $273 | | 1
Fluorescent slide | FSK5 | https://www.thorlabs.com/thorproduct.cfm?partnumber=FSK5 $20 | | 1
Black Aluminium Foil Tape | AT205-1.0 | https://www.thorlabs.us/thorProduct.cfm?partNumber=T205-1.0 $35 | | 1
Safety Goggles | NoIR ML1 Filter for Multiple Laser Diodes | https://safetyglassesusa.com/products/nl-ml1-html?variant=40169833857108&cmp_id=18259498523&adg_id=&kwd=&device=c&gad_source=1&gclid=Cj0KCQjwtsy1BhD7ARIsAHOi4xY7sfWrRyzZkN7bREsC5d24bBn0M8J_CNregOlg-xVHpzjeuJ0I6BUaAlG7EALw_wcB $190 | | 3

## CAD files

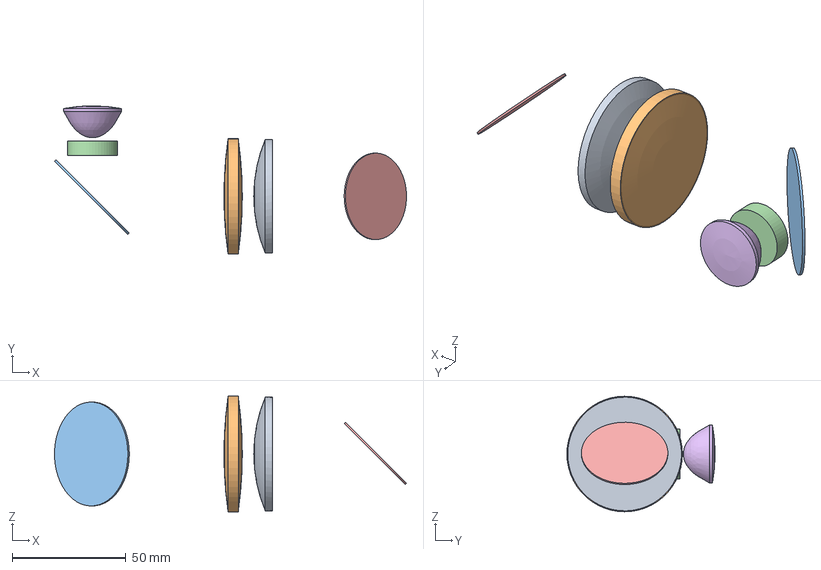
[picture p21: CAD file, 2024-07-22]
zemax/Collection/collection_optics.stp
154.7 x 65.2 x 50.8 mm
surfaces 5,6
surfaces 7,8
mirror 10
surfaces 12,13
mirror 3
surfaces 14,15

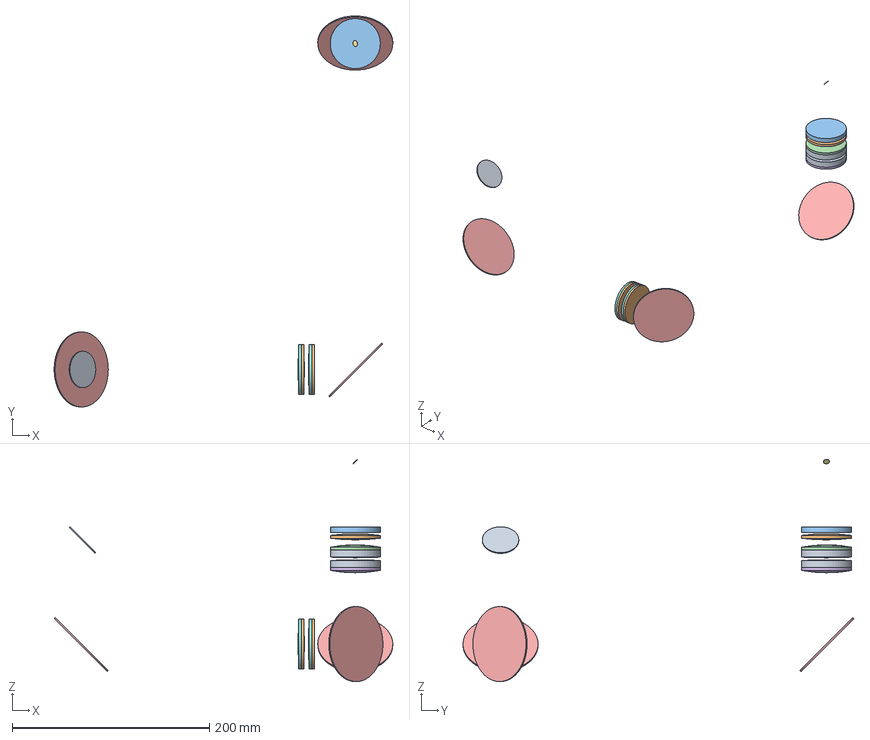
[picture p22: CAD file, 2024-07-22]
zemax/Excitation/excitation_twinkle.stp
343.5 x 396.6 x 225.4 mm
surfaces 14,15
surfaces 12,13
surfaces 9,10
surfaces 7,8
surfaces 11,12
mirror 21
mirror 18
surfaces 15,16
mirror 4
surfaces 24,25
surfaces 28,29
surfaces 34,35
surfaces 23,24
surfaces 27,28
mirror 32

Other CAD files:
cad/FullAssembly/02242020_ScanLenses (1).ipt
cad/FullAssembly/02242020_ScanLenses.ipt
cad/FullAssembly/107405-09 - Top Skin 1219.2 x 2438.4mm_107405-09 With Holes.ipt
cad/FullAssembly/107419 - Table Base Skin 2438.4 x 1219.2.ipt
cad/FullAssembly/107437 - Corner Angle 210mm Table.ipt
cad/FullAssembly/107442 - Printed Desktop 199mm Width_107442-04 - 8'' Table.iam
cad/FullAssembly/107442 - Printed Desktop 199mm Width_107442-04 - 8'' Table_1.iam
cad/FullAssembly/107463 - Desktop Roll Cut to 199mm_30000mm.ipt
cad/FullAssembly/107463 - Desktop Roll Cut to 199mm_IMPERIAL - 4'' Table.ipt
cad/FullAssembly/107538 - Side Panel 4'' x 210mm Table.iam
cad/FullAssembly/107538 - Side Panel 4'' x 210mm Table_1.iam
cad/FullAssembly/107541 - Side Panel 8'' x 210mm Table.iam
cad/FullAssembly/107541 - Side Panel 8'' x 210mm Table_1.iam
cad/FullAssembly/107941  Table Side Panel End Cap.ipt
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

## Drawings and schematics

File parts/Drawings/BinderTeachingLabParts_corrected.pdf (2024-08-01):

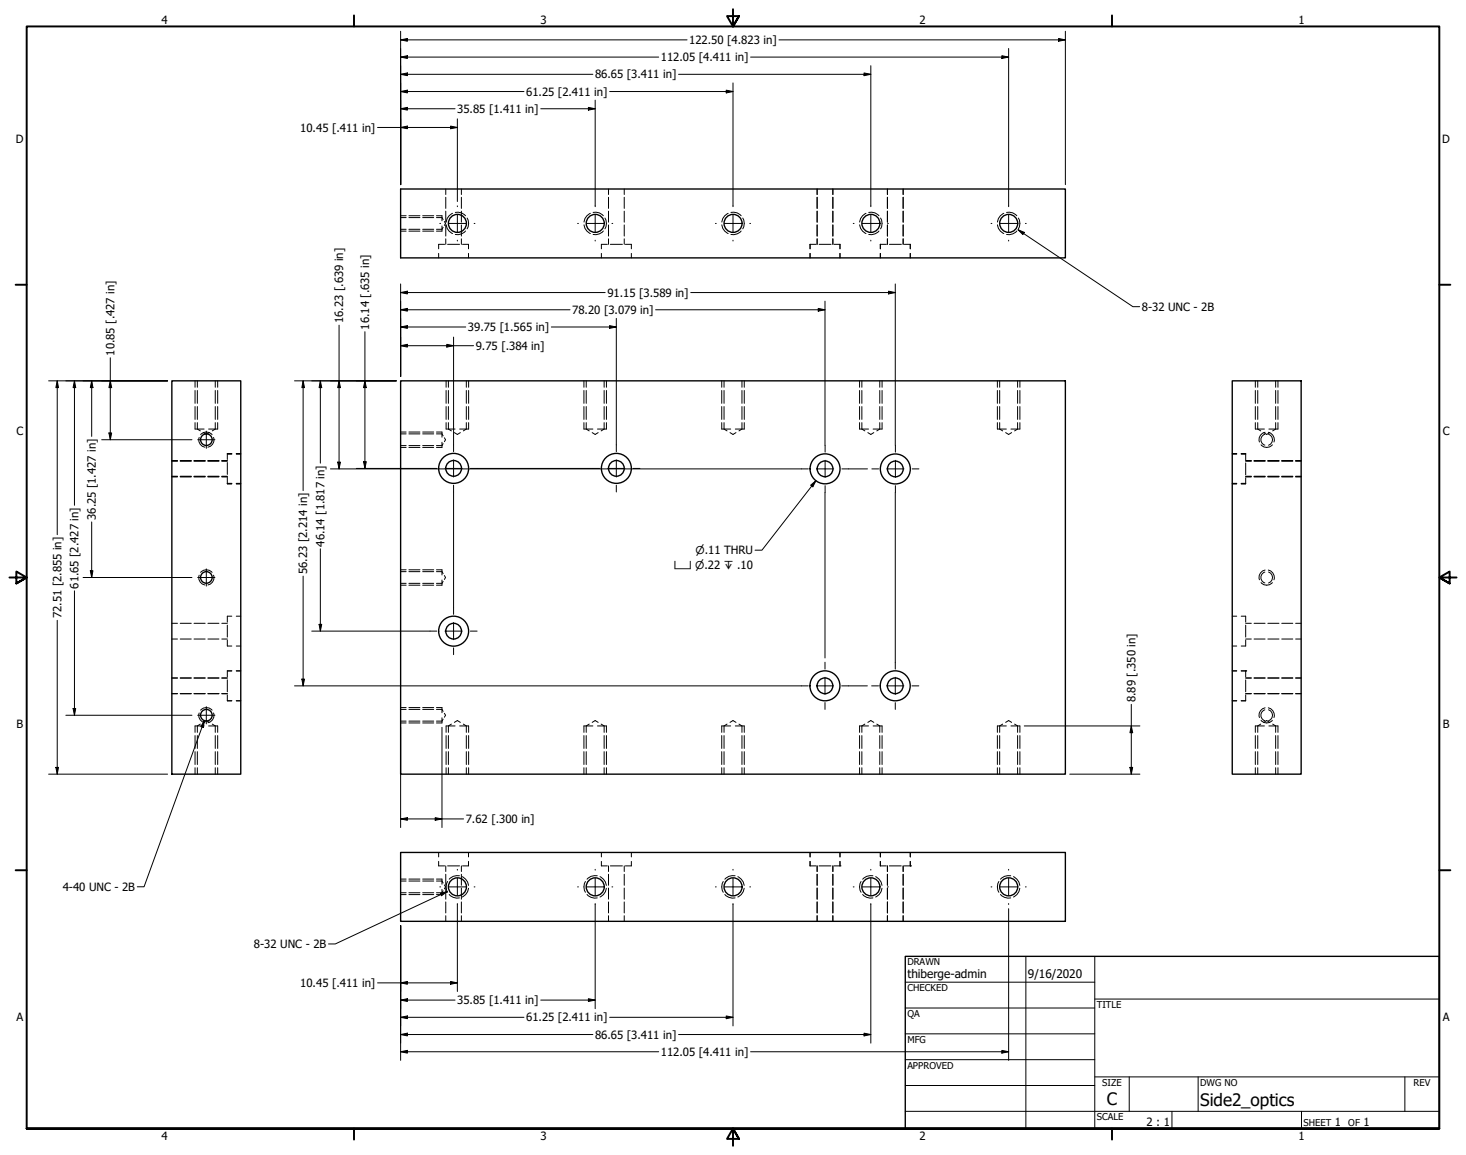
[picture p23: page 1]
8-32 UNC - 2B; 4-40 UNC - 2B

DRAWN thiberge-admin | 9/16/2020

CHECKED

MFG

APPROVED

SIZE C | DWG NO Side2_optics | REV

SCALE | | SHEET 1 OF 1

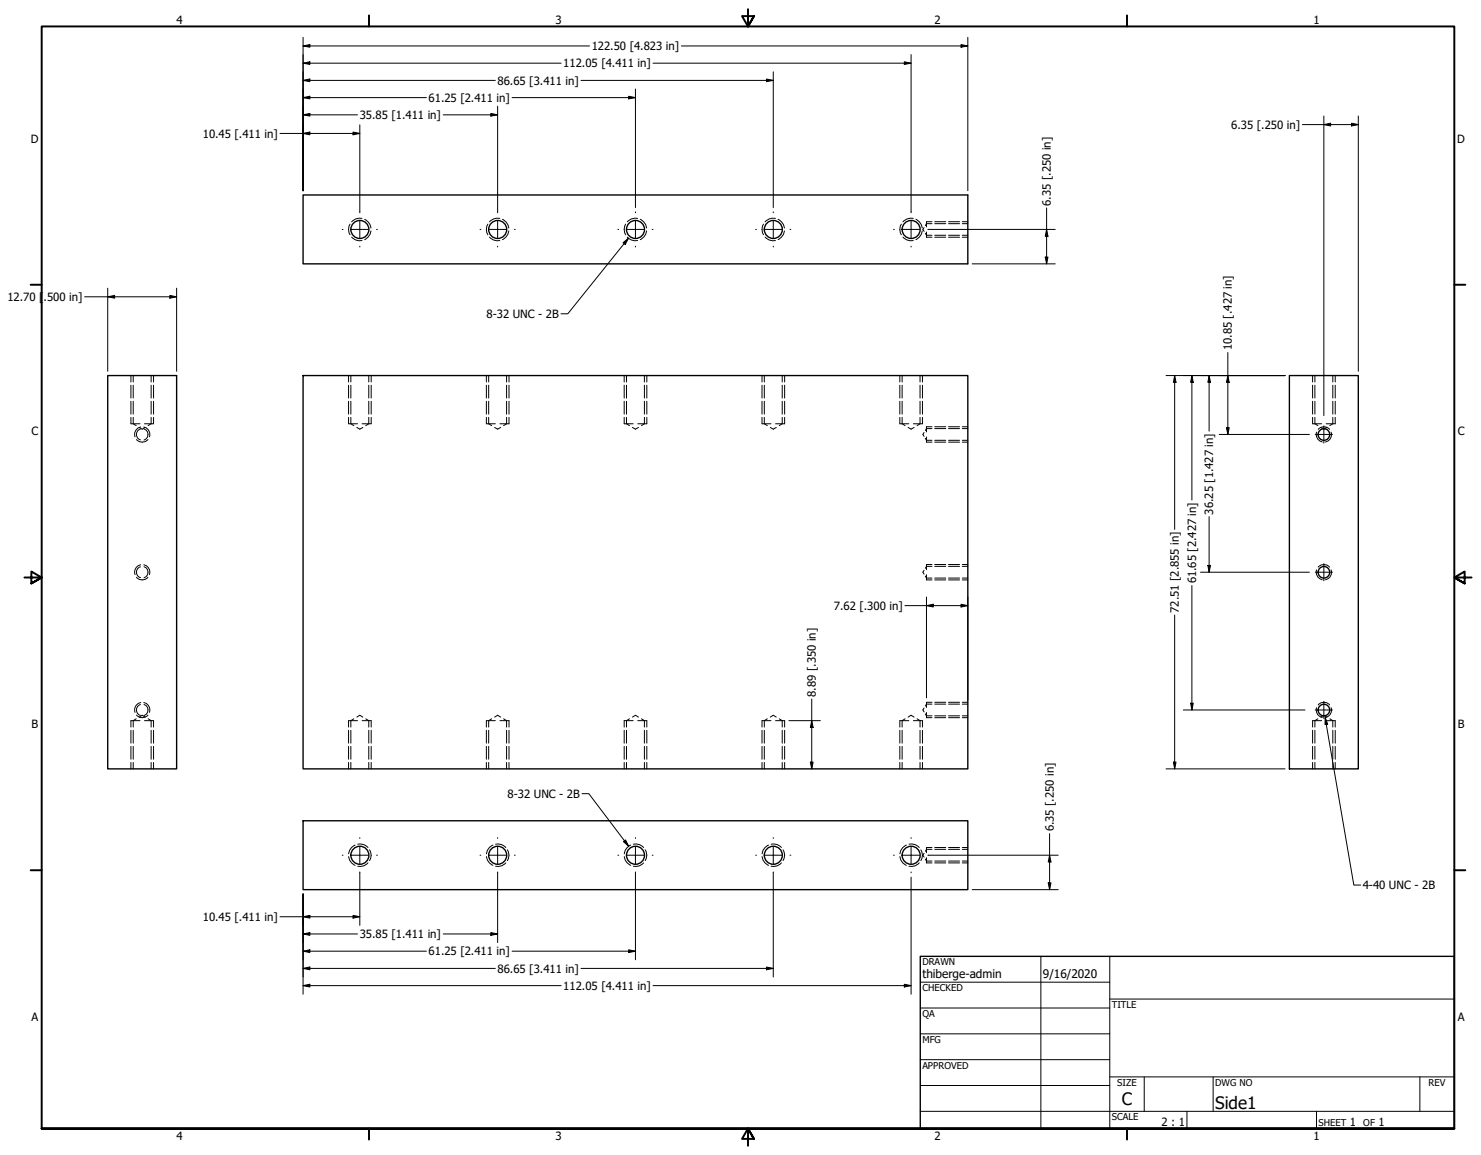
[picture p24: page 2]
8-32 UNC - 2B; 4-40 UNC - 2B

DRAWN thiberge-admin | 9/16/2020

CHECKED

MFG

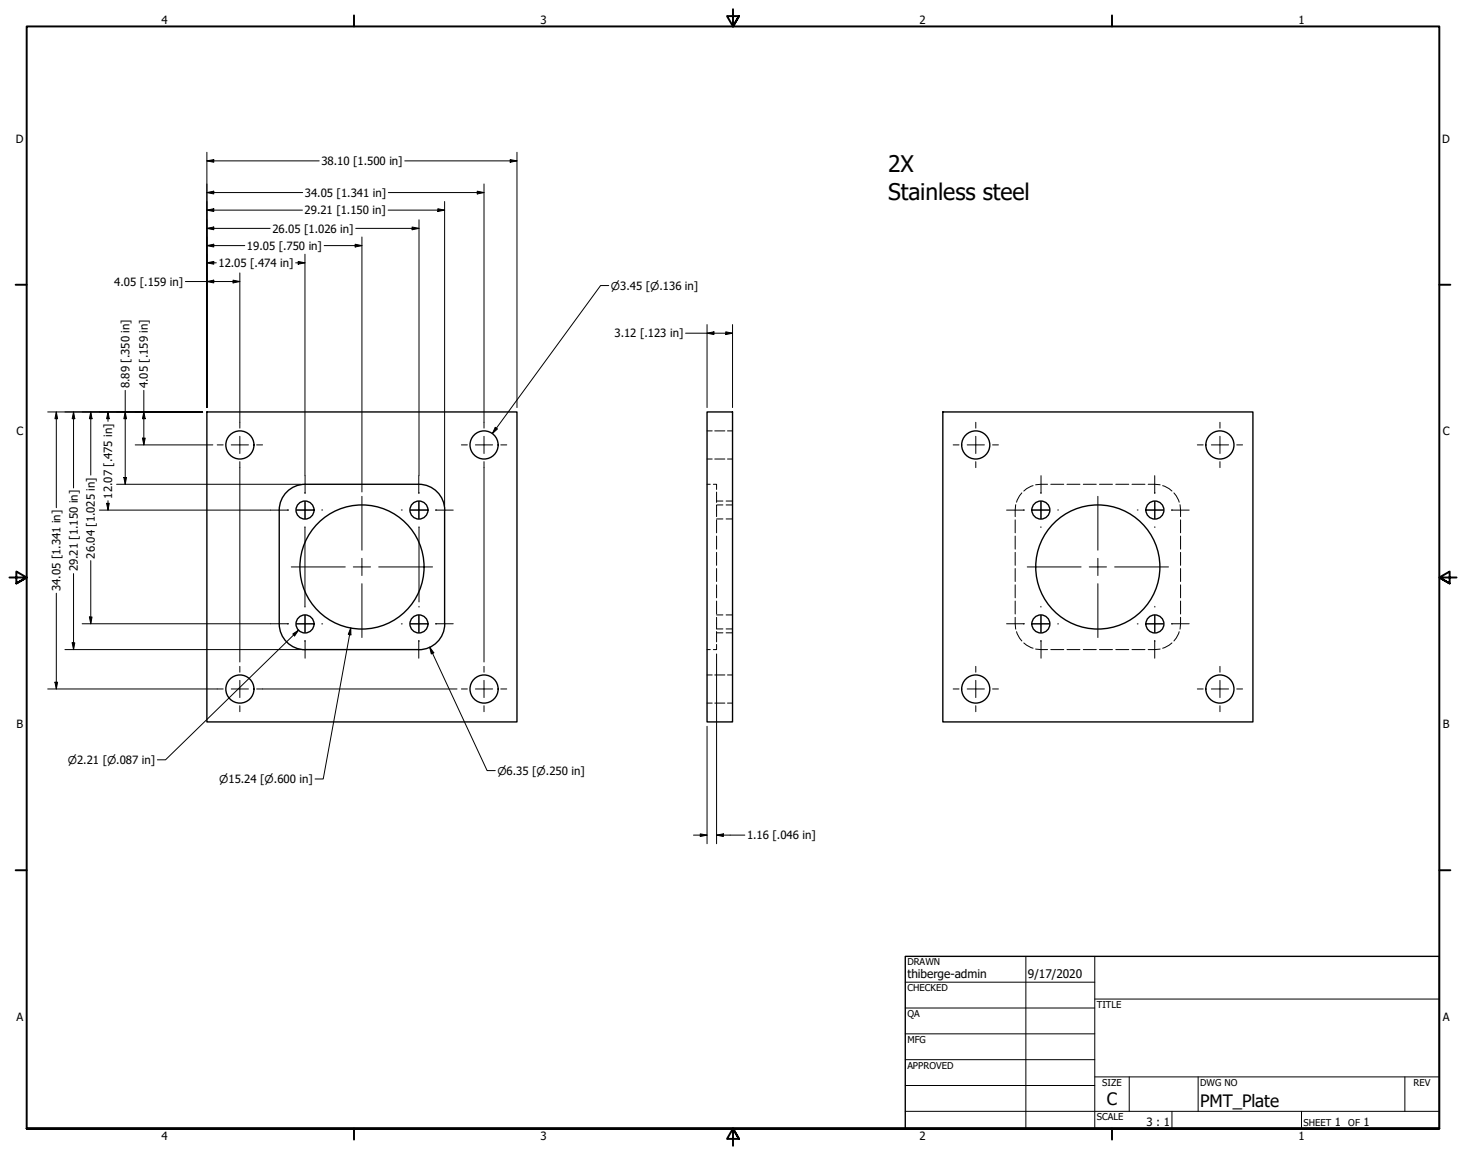
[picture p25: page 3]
Stainless steel

DRAWN thiberge-admin | 9/17/2020

CHECKED

MFG

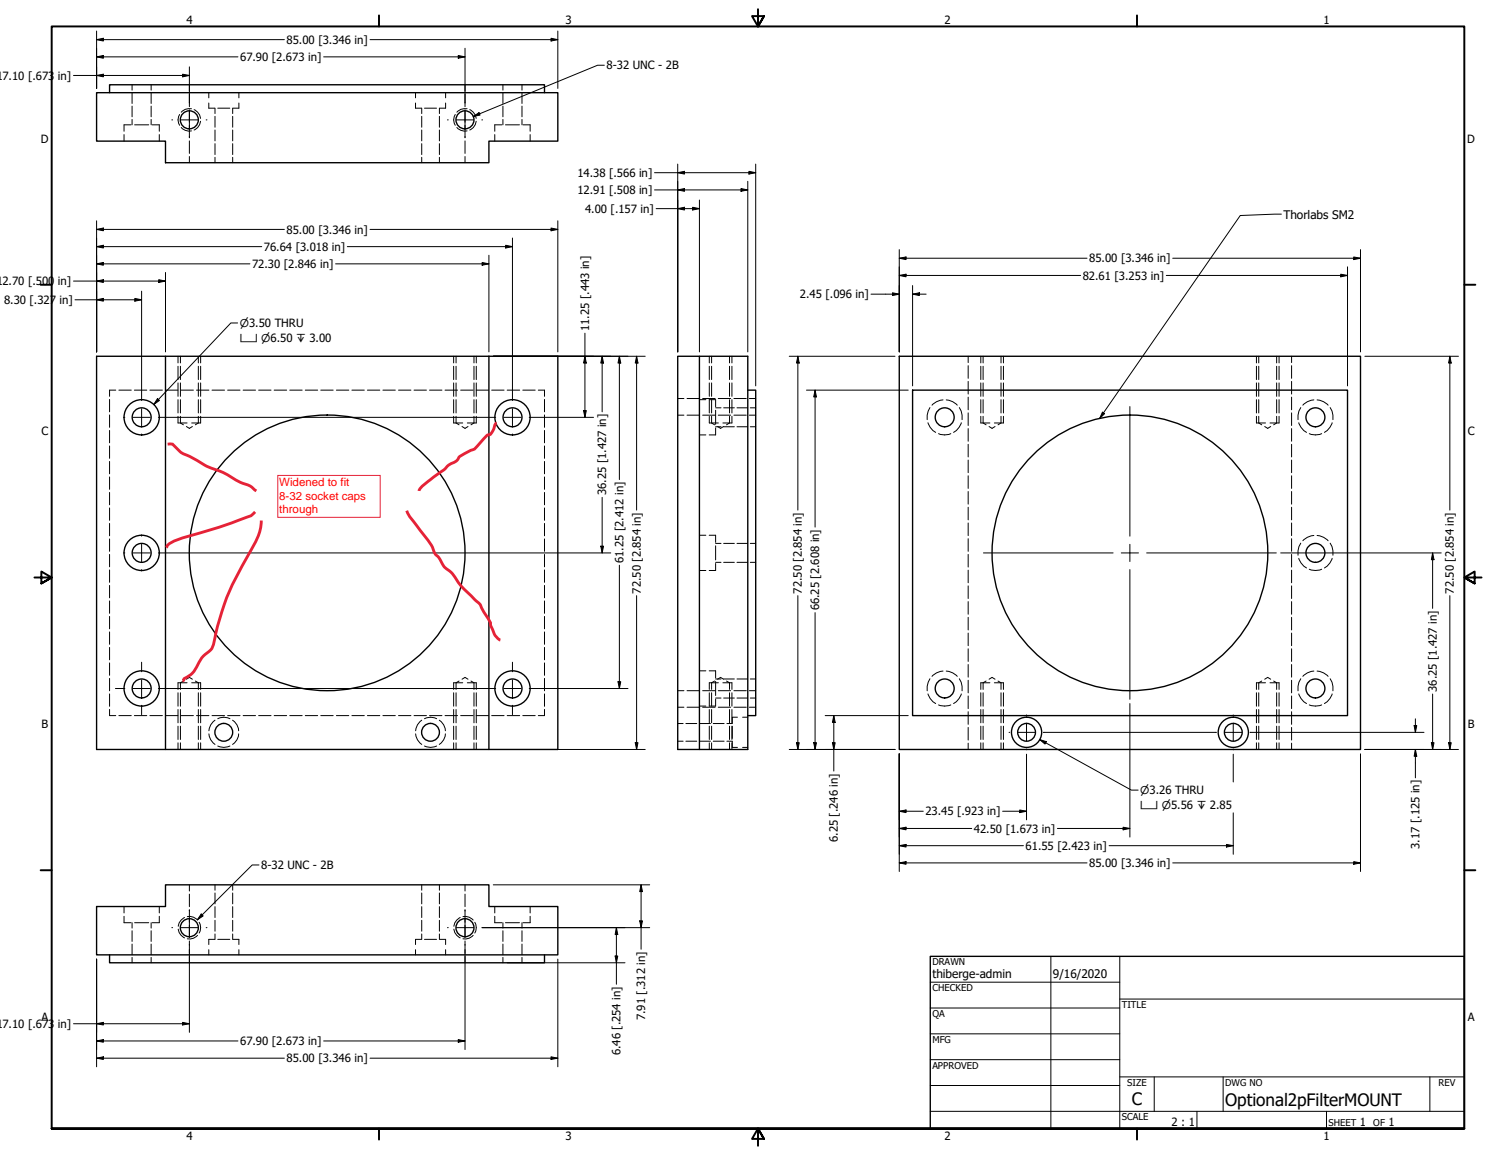
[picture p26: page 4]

S I Z E | D W G N O O p t i o n al2 p F ilt e r M O U N T | R E V

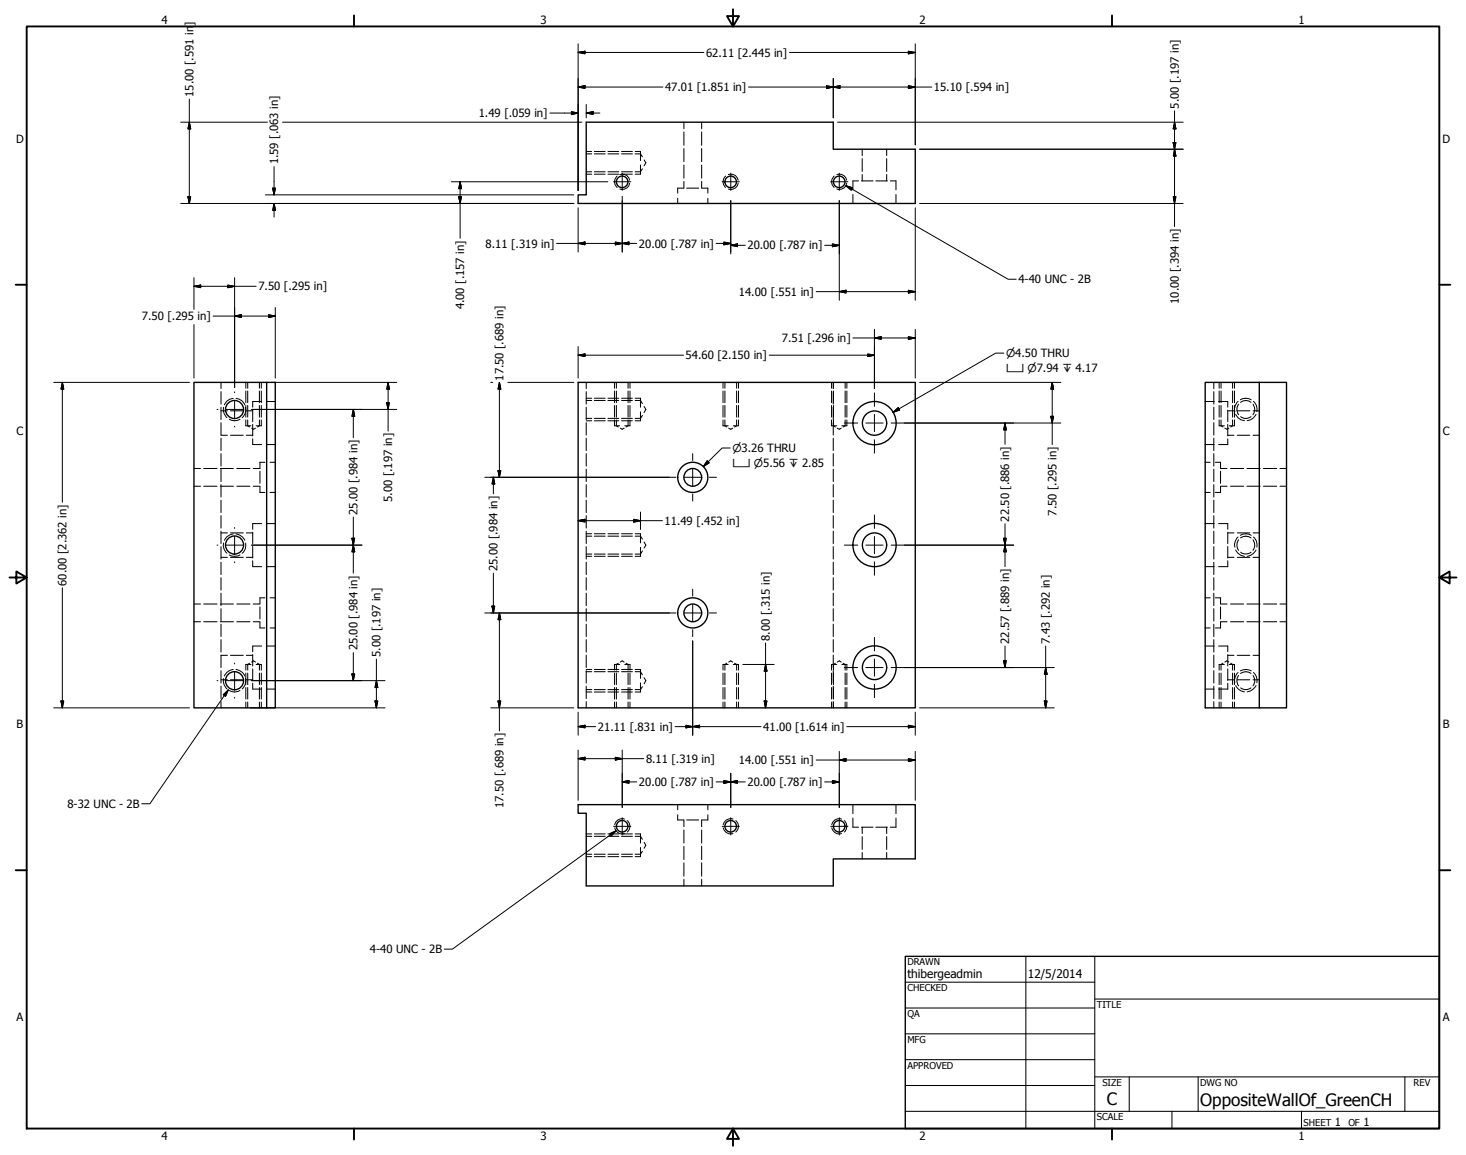
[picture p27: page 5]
4-40 UNC - 2B; 8-32 UNC - 2B

DRAWN thibergeadmin | 12/5/2014

CHECKED

MFG

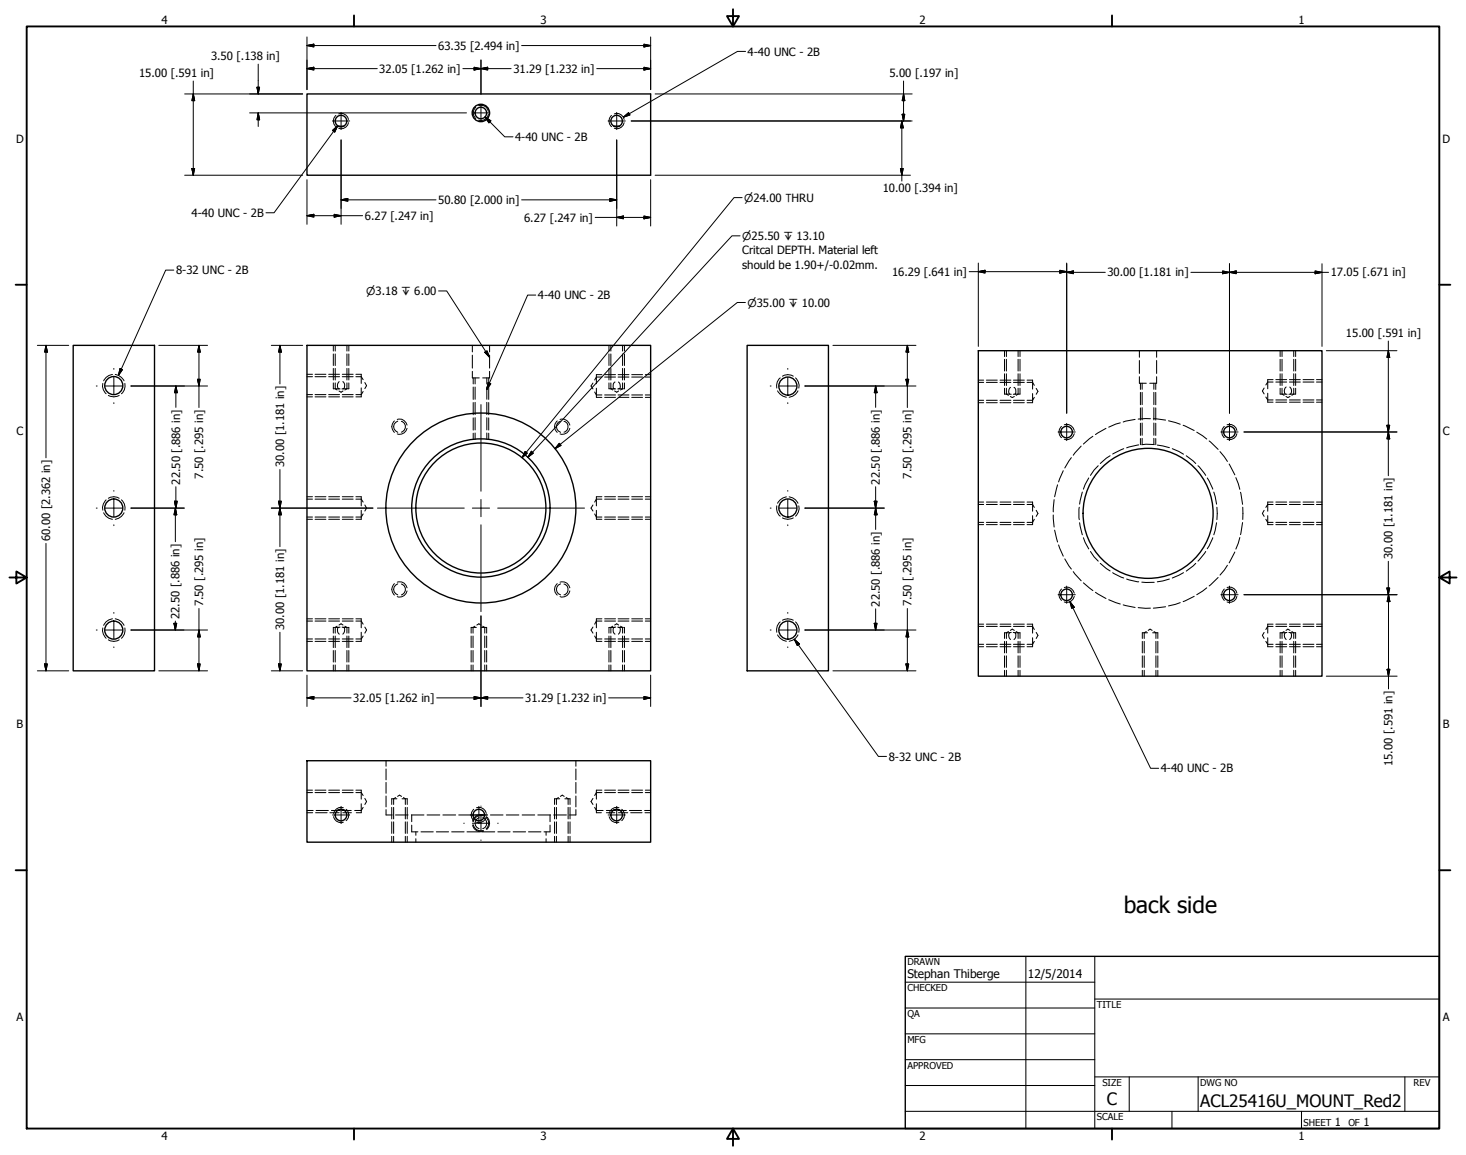
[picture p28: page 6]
8-32 UNC - 2B; 4-40 UNC - 2B; back side

Critcal DEPTH. Material left
should be 1.90+/-0.02mm.

DRAWN Stephan Thiberge | 12/5/2014

CHECKED

MFG

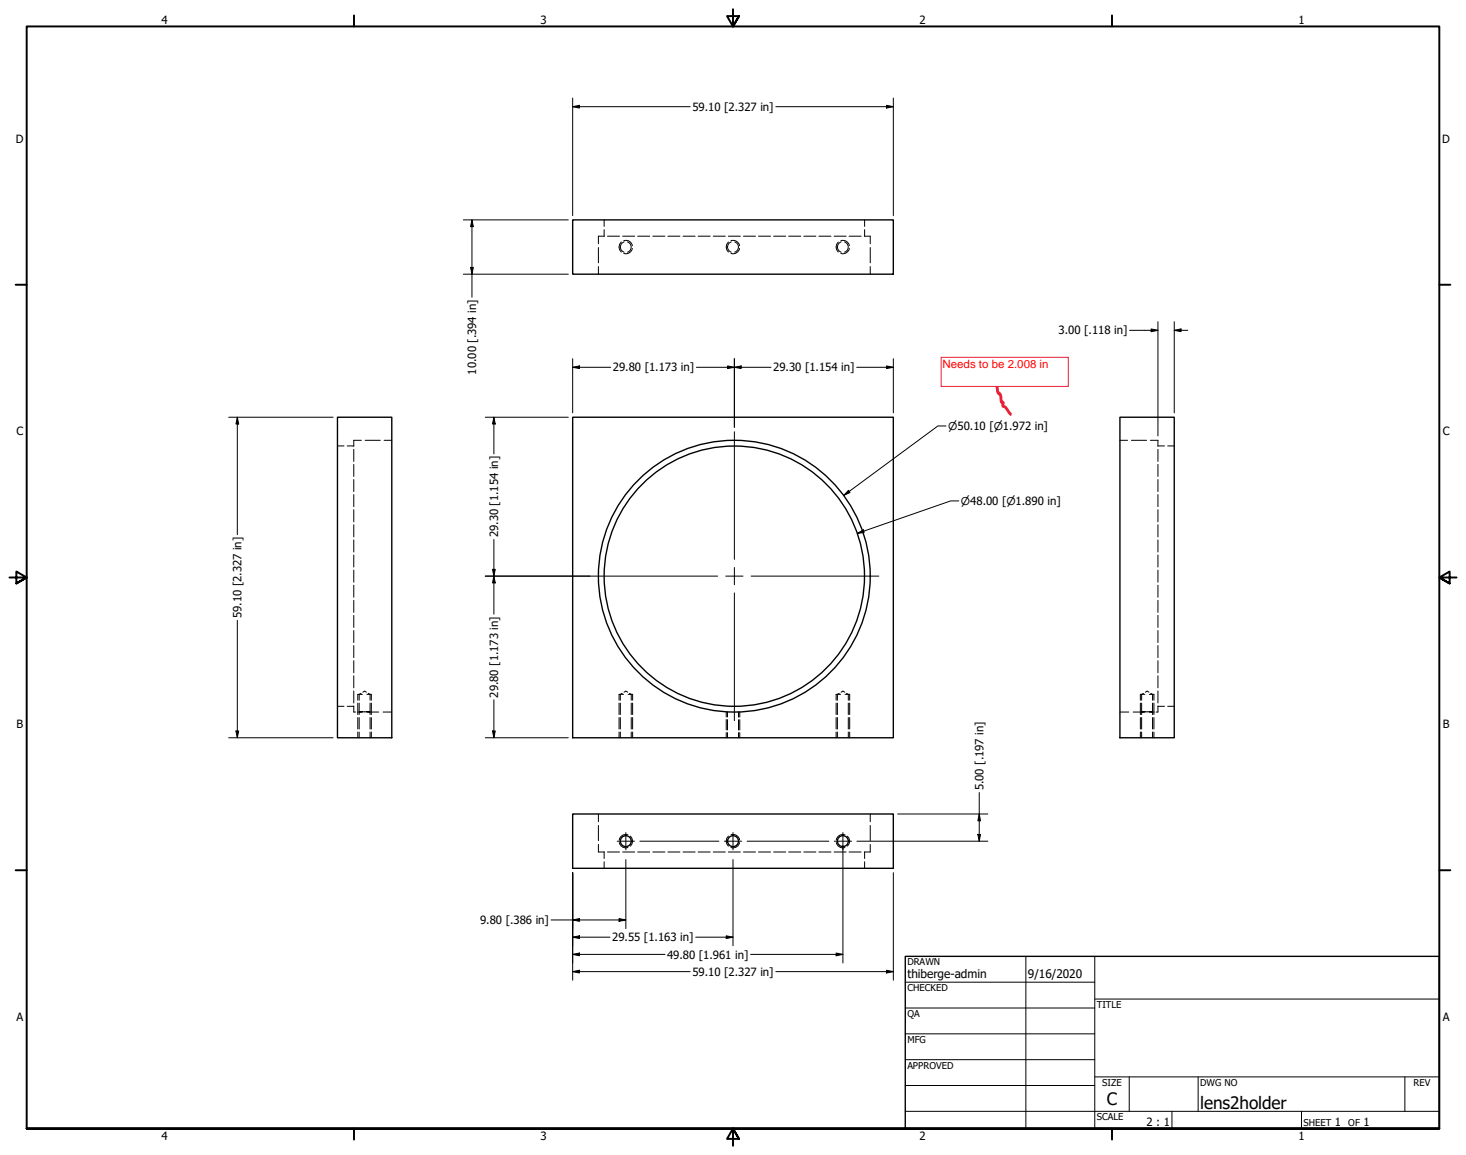
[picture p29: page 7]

DRAWN thiberge-admin | 9/16/2020

CHECKED

MFG

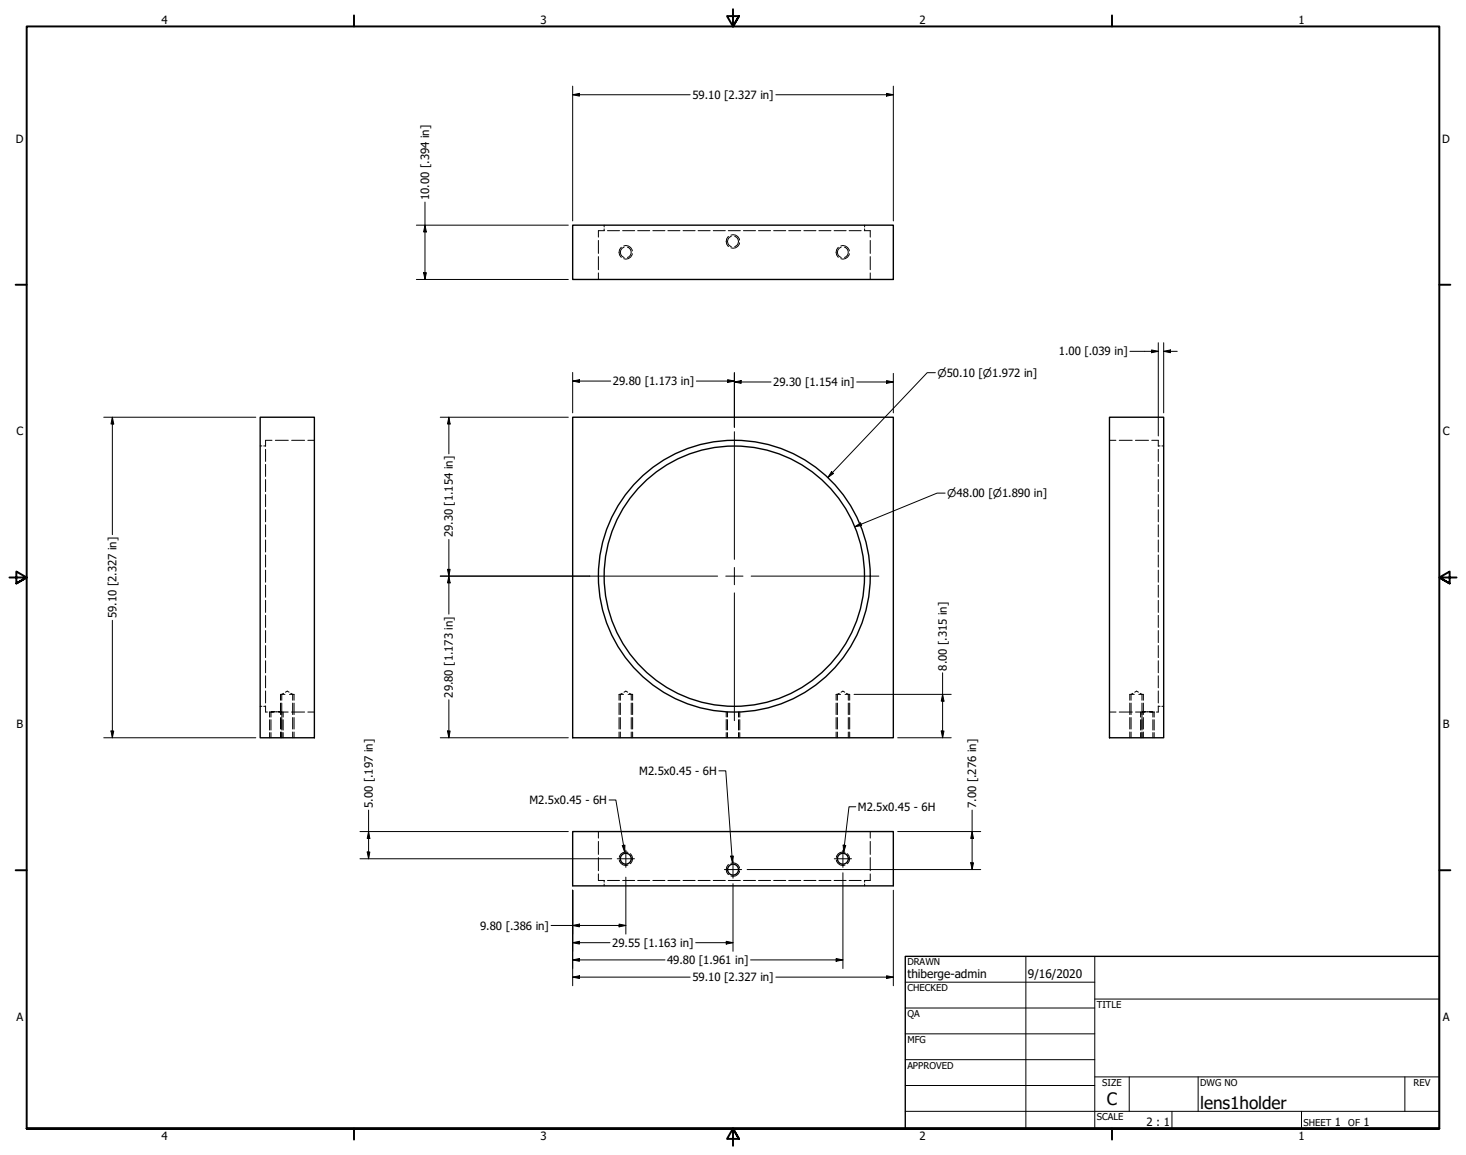
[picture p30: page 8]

DRAWN thiberge-admin | 9/16/2020

CHECKED

MFG

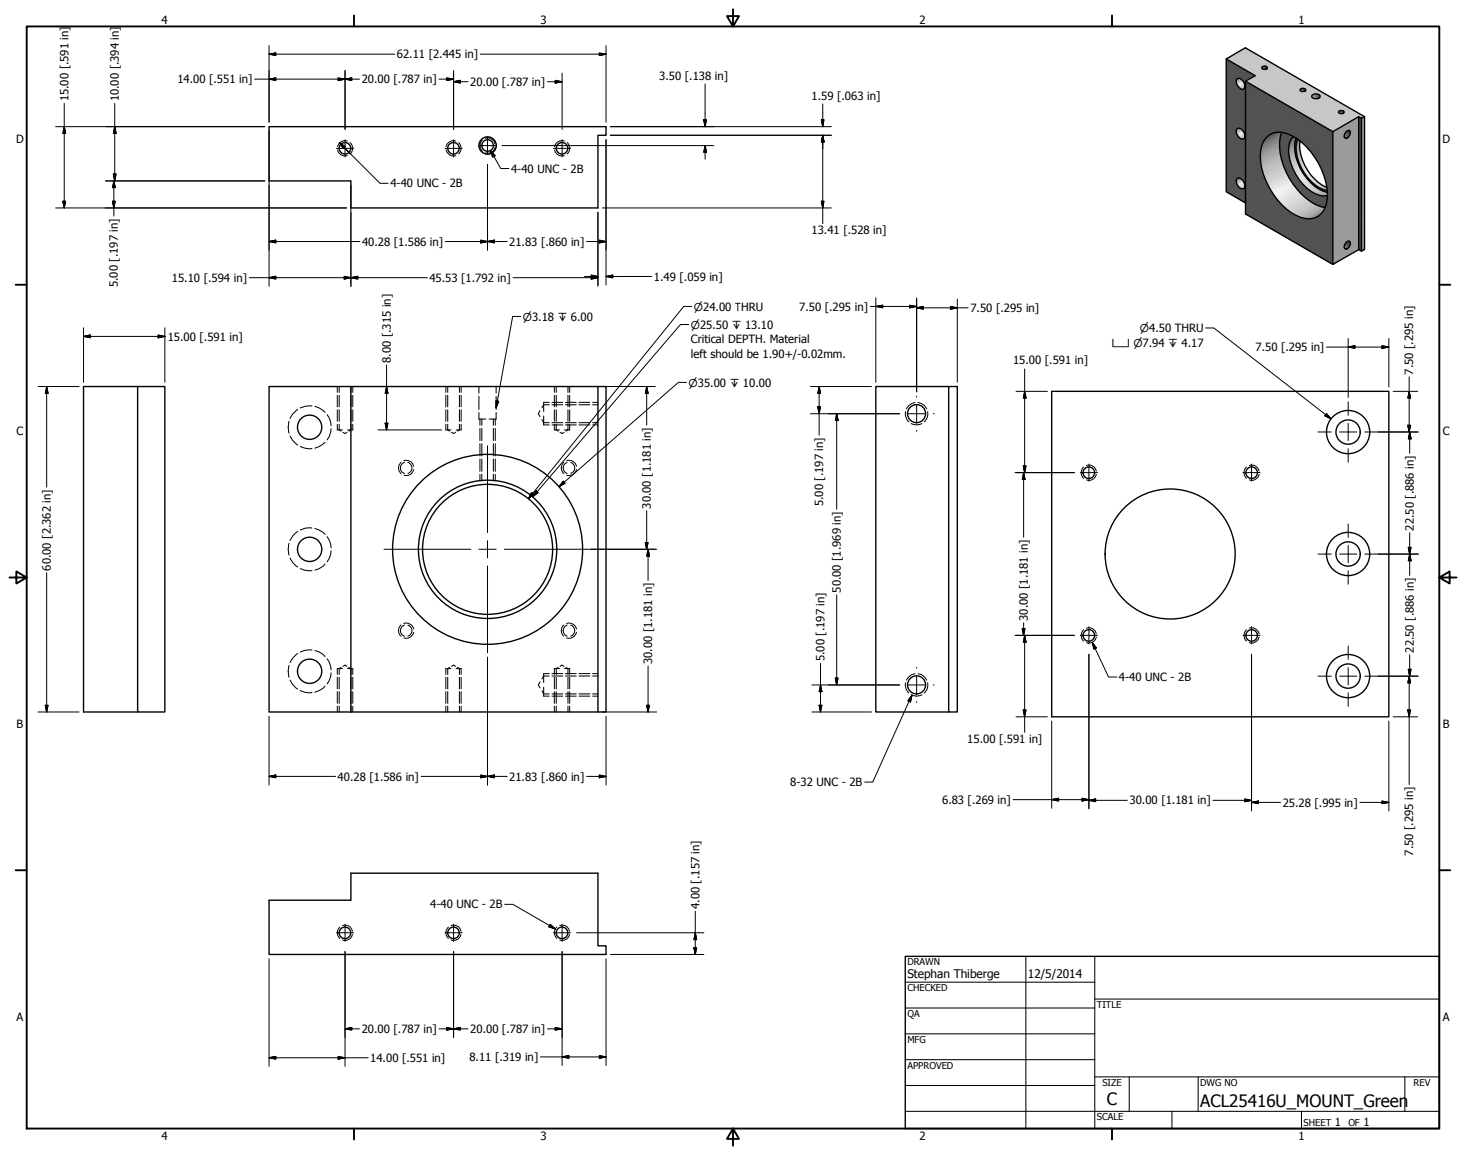
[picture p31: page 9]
4-40 UNC - 2B; 8-32 UNC - 2B

24.00 6HRU
Critical DEPTH. Material
left should be 1.90+/-0.02mm.

4-40 UNC - 2B

DRAWN Stephan Thiberge | 12/5/2014

CHECKED

MFG

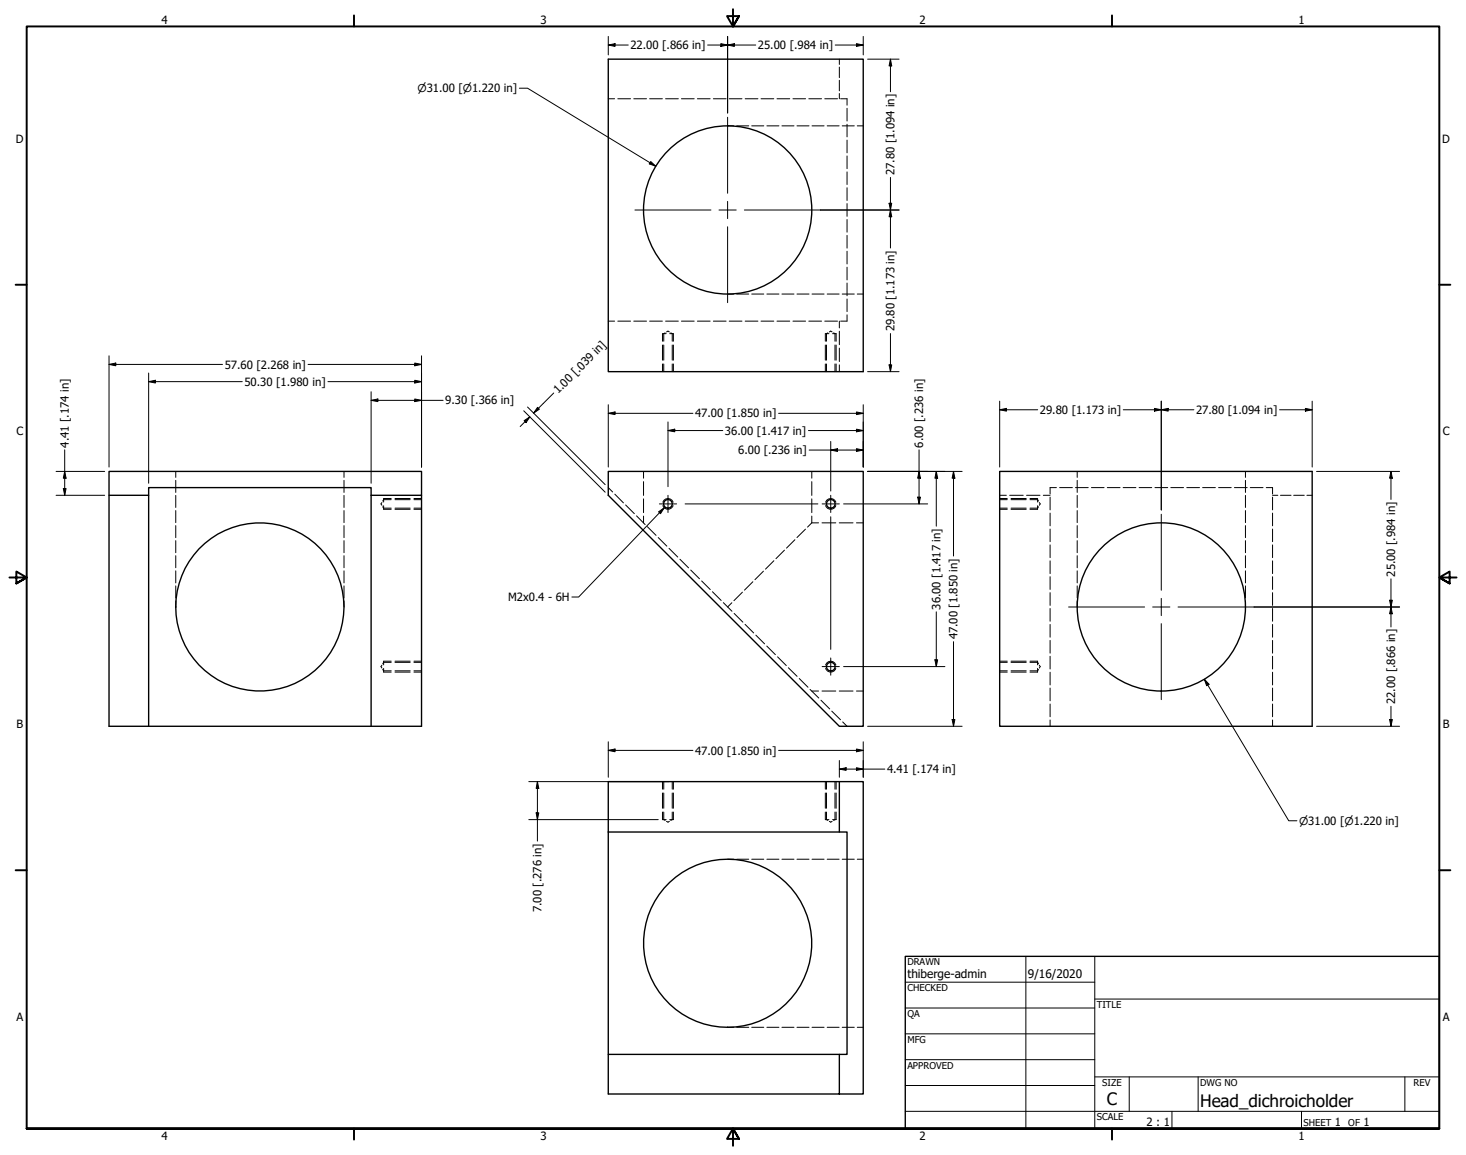
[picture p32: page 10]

DRAWN thiberge-admin | 9/16/2020

CHECKED

MFG

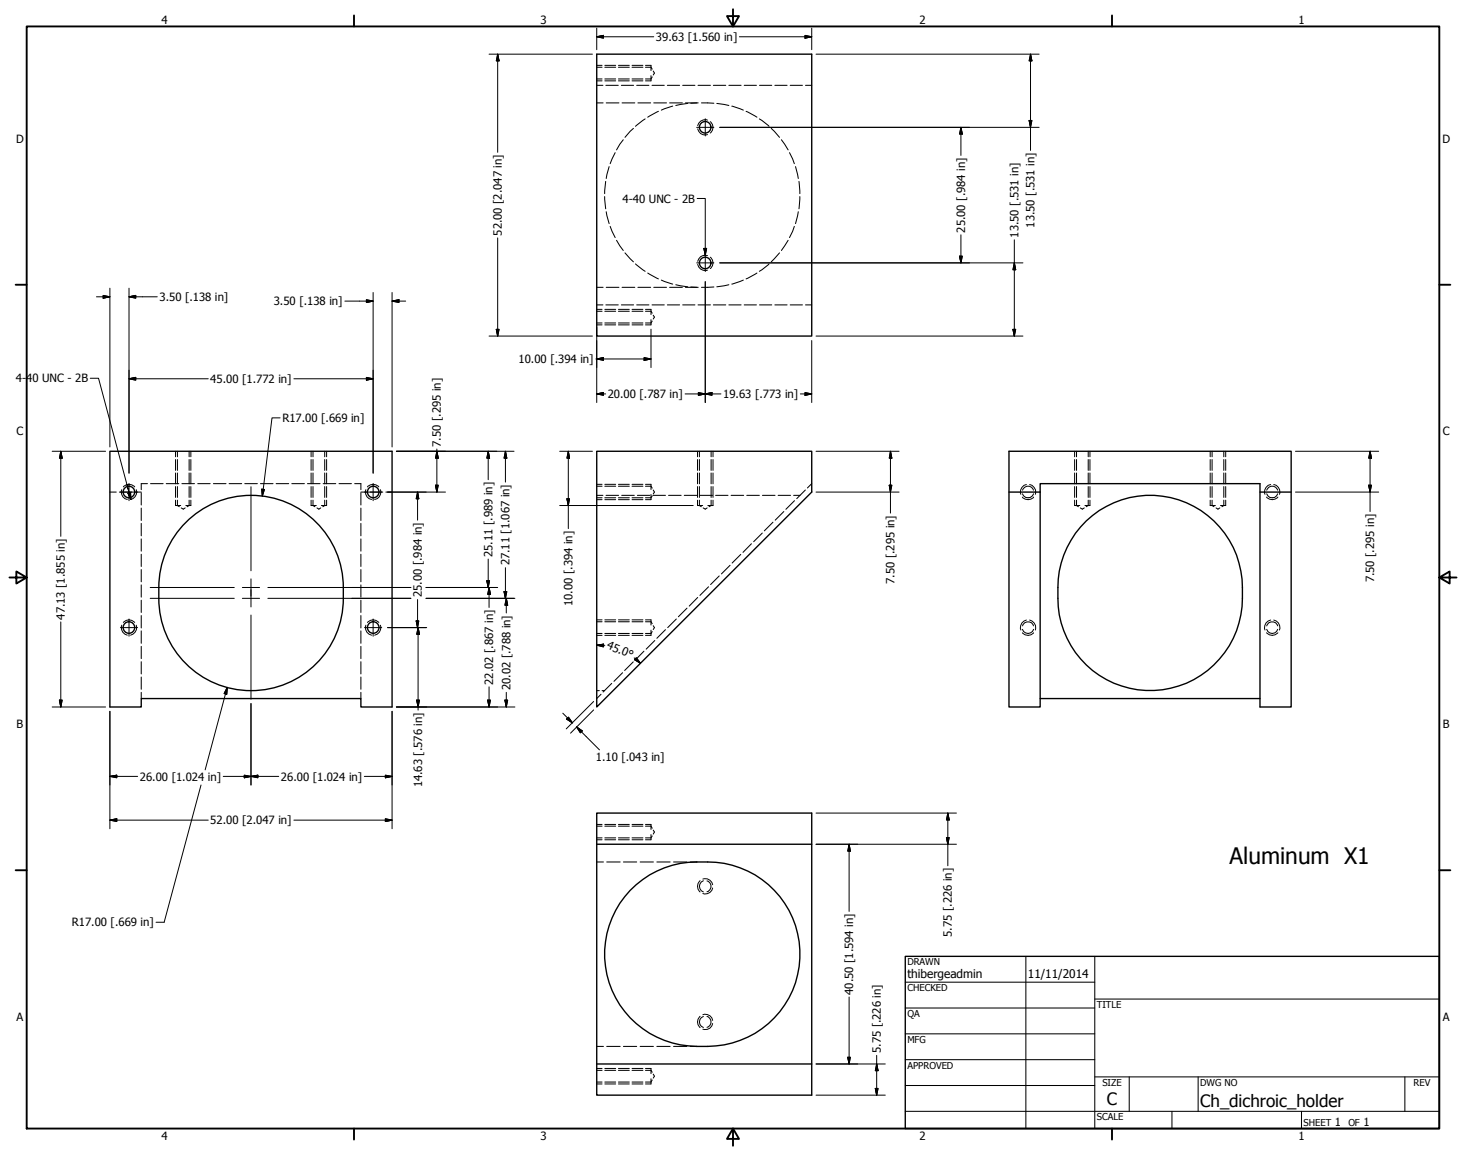
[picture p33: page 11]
4-40 UNC - 2B; Aluminum X1

DRAWN thibergeadmin | 11/11/2014

CHECKED

MFG

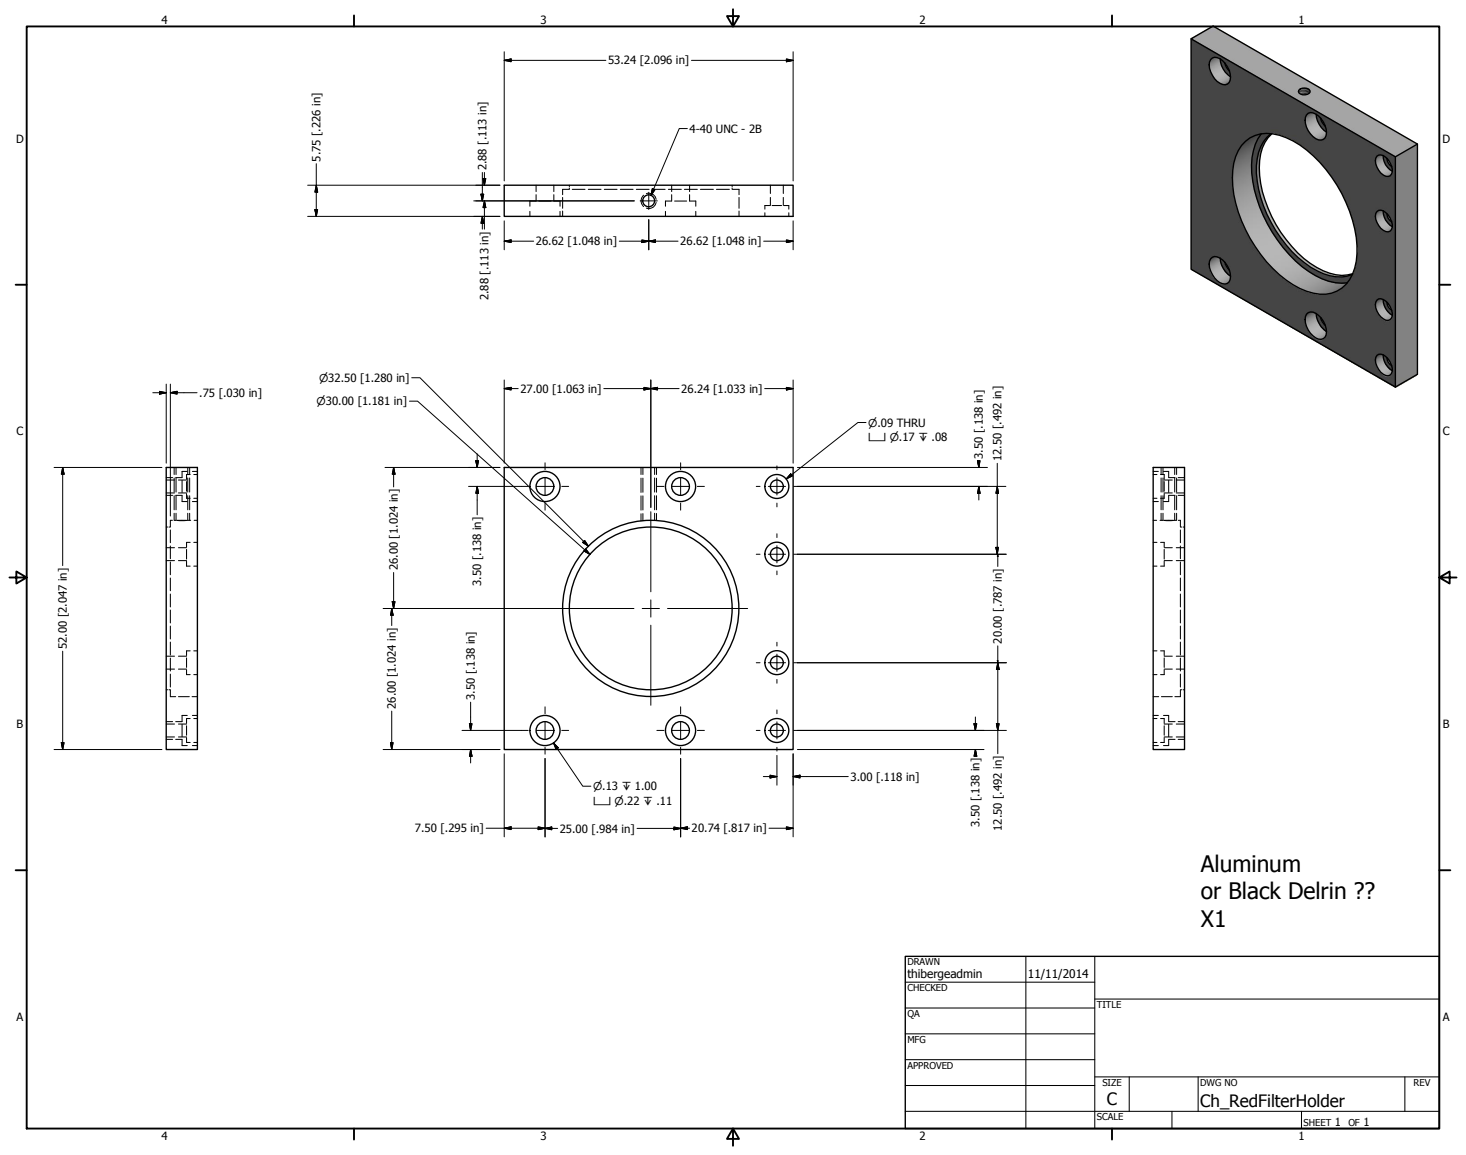
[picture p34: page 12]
4-40 UNC - 2B; or Black Delrin ??

DRAWN thibergeadmin | 11/11/2014

CHECKED

MFG

4-40 UNC - 2B; 2-56 UNC - 2B

DRAWN thibergeadmin | 11/11/2014

CHECKED

MFG

Aluminum X2

DRAWN thibergeadmin | 11/10/2014

CHECKED

MFG


DRAWN thiberge-admin | 9/16/2020

CHECKED

MFG

5/16-18 UNC - 2B

DRAWN thiberge-admin | 9/16/2020

CHECKED

MFG

4-40 UNC - 2B

DRAWN thiberge-admin | 9/16/2020

CHECKED

MFG

1/4-20 UNC - 2B; Modified 12in by 12in Thorlabs breadboard

DRAWN thiberge-admin | 12/6/2020

CHECKED

MFG


DRAWN thiberge-admin | 12/6/2020

CHECKED

MFG

XT95-750-Step

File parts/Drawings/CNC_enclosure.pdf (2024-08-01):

SHEET 1 OF 1; DRAWN; CHECKED; MFG; APPROVED; Stephan Thiberge; DWG NO CNC_enclosure; TITLE; SIZE C; SCALE; REV; 4-40 UNC - 2B; P.27 THRU X P.44 Z .15; 1.035-40 UNS - 2B; "Thorlabs SM1"

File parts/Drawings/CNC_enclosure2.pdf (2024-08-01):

SHEET 1 OF 1; DRAWN; CHECKED; MFG; APPROVED; thiberge-admin; DWG NO CNC_enclosure2; TITLE; SIZE C; SCALE; REV; 4-40 UNC - 2B -depth .16

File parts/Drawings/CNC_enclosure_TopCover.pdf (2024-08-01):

SHEET 1 OF 1; DRAWN; CHECKED; MFG; APPROVED; Stephan Thiberge; DWG NO CNC_enclosure_TopCover; TITLE; SIZE C; SCALE; REV; P.13 THRU X P.22 Z .11; P.15 THRU X P.28 Z .14

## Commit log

2024-07-22 Added readme and zemax files
    [collection_optics.stp, excitation_twinkle.stp]
2024-08-01 Added Inventor export including parts
    [02242020_ScanLenses (1).ipt, 02242020_ScanLenses.ipt, 107405-09 - Top Skin 1219.2 x 2438.4mm_107405-09 With Holes.ipt, 107419 - Table Base Skin 2438.4 x 1219.2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]
2024-08-10 updated CAD files
    [02242020_ScanLenses (1).ipt, 02242020_ScanLenses.ipt, 107405-09 - Top Skin 1219.2 x 2438.4mm_107405-09 With Holes.ipt, 107419 - Table Base Skin 2438.4 x 1219.2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]
2024-09-11 updated CAD files to latest version
    [02242020_ScanLenses (1).ipt, 02242020_ScanLenses.ipt, 107405-09 - Top Skin 1219.2 x 2438.4mm_107405-09 With Holes.ipt, 107419 - Table Base Skin 2438.4 x 1219.2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]
2024-09-11 article/documentation and updated readme
    [ScopeExpenses.xlsx]
2024-09-17 Updated CAD files with Laser shields + Tubing
    [02242020_ScanLenses (1).ipt, 02242020_ScanLenses.ipt, 107405-09 - Top Skin 1219.2 x 2438.4mm_107405-09 With Holes.ipt, 107419 - Table Base Skin 2438.4 x 1219.2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]
2024-09-19 updates to bill of materials
    [ScopeExpenses.xlsx]
2024-09-19 Stephan's edits for Article + Supplement
    [ScopeExpenses.xlsx]
2025-02-20 updated cad files:
    removed unnecessary part duplicates;
    updated lens size in collection options to 2 inch.
    [02242020_ScanLenses (1).ipt, 02242020_ScanLenses.ipt, 107405-09 - Top Skin 1219.2 x 2438.4mm_107405-09 With Holes.ipt, 107419 - Table Base Skin 2438.4 x 1219.2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]

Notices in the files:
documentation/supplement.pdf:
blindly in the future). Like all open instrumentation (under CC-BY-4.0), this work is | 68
